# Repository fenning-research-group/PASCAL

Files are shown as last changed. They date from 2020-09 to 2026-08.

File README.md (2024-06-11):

# Perovskite Automated Spin Coat Assembly Line (PASCAL)

## Motivation

PASCAL is an automated platform for spin coating and annealing thin films onto small (>2x2 cm) substrates, aimed af increasing experimental throughput in the pursuit of designing better perovskite solar cells. Perovskite solar cells are infinitely tunable, as they can be formed with combinations of nearly half of the periodic table, presenting the excitement of limitless possibilities and the curse of dimensionality. With PASCAL, we aim to increase our experimental search rate by orders of magnitude, enabling a more systematic and exhaustive approach toward exploring the vast compositional space of interest for solar cell design.

## Hardware

### CAD schematics of PASCAL

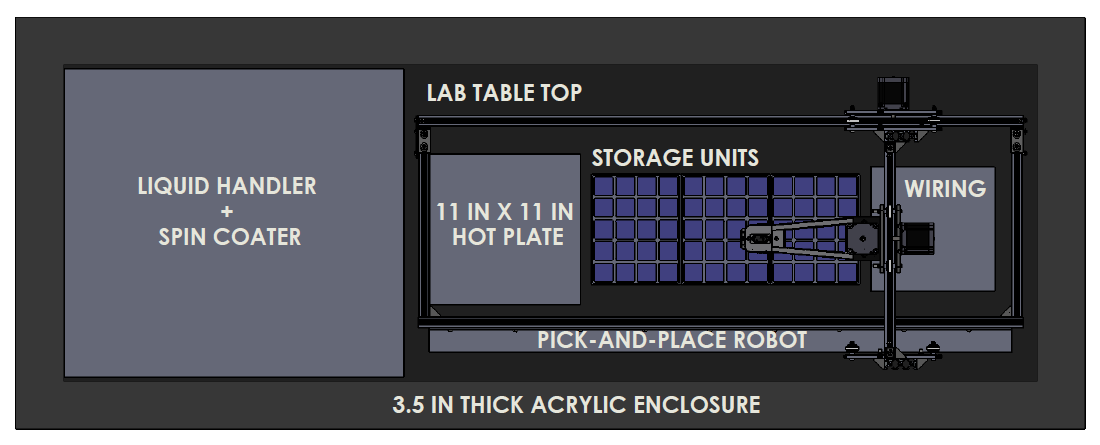
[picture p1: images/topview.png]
top view

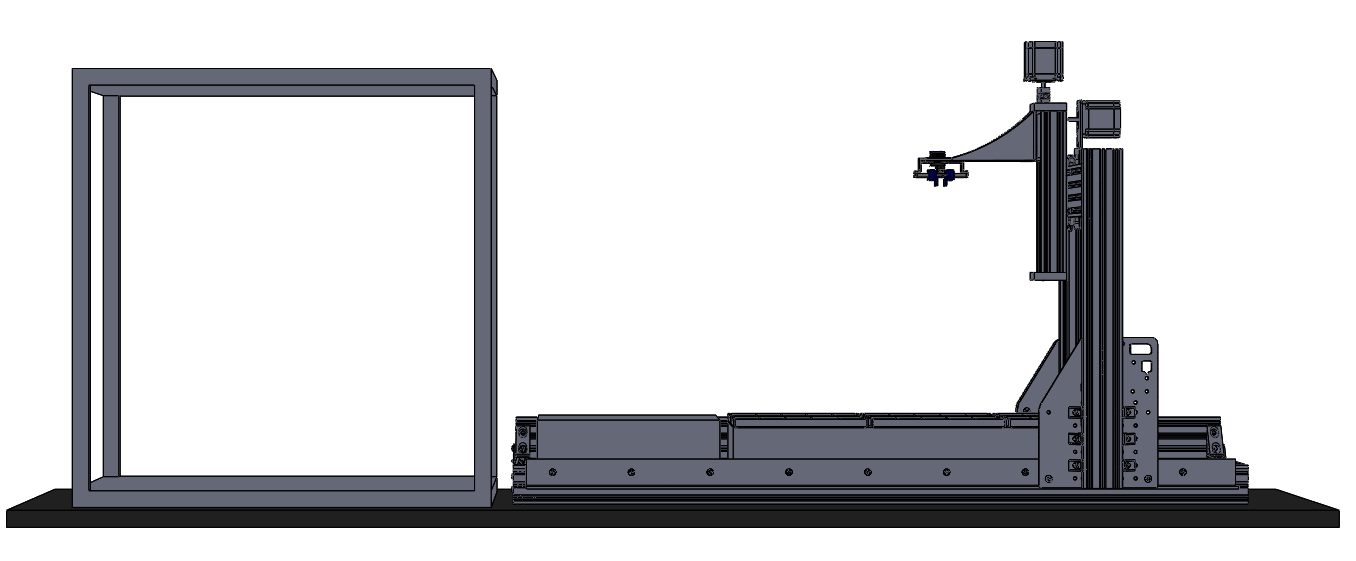
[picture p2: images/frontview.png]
front view


### Liquid handler preparing precursor solution mixtures for a compositional search

liquid handler preparing solutions for a composition spread

### Liquid handler + spincoater working in conjunction to deposit solution onto substrate.

spin coating one sample

### Automated Full Sample Fabrication + Characterization Timelapse

https://github.com/fenning-research-group/PASCAL/assets/49666626/01028334-c0f0-4b86-ad78-245d9399b324

## Experimental Planning

- Computed material properties -> manifold embedding / dimensionality reduction into "behavior space"

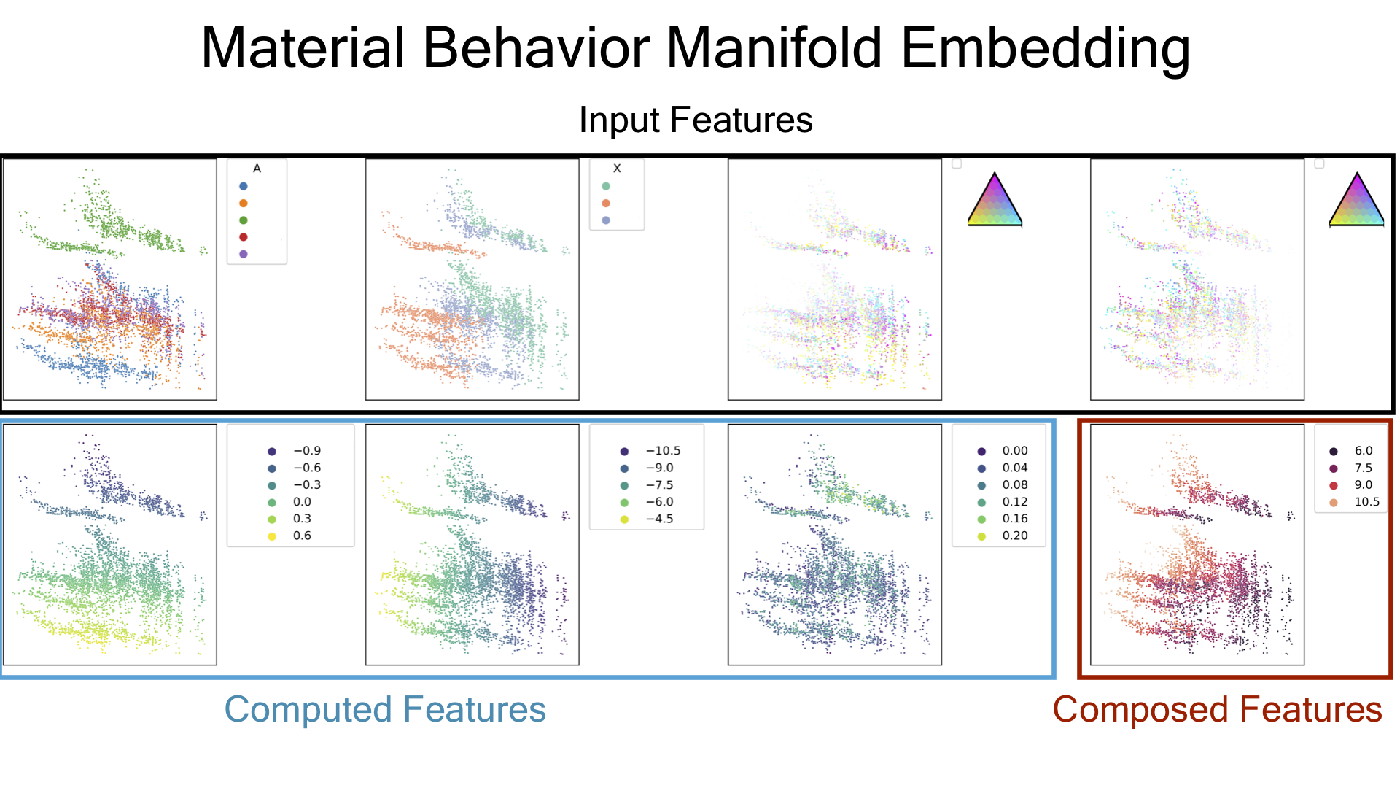
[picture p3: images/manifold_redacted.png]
manifold embedding


### Hardware Scheduling

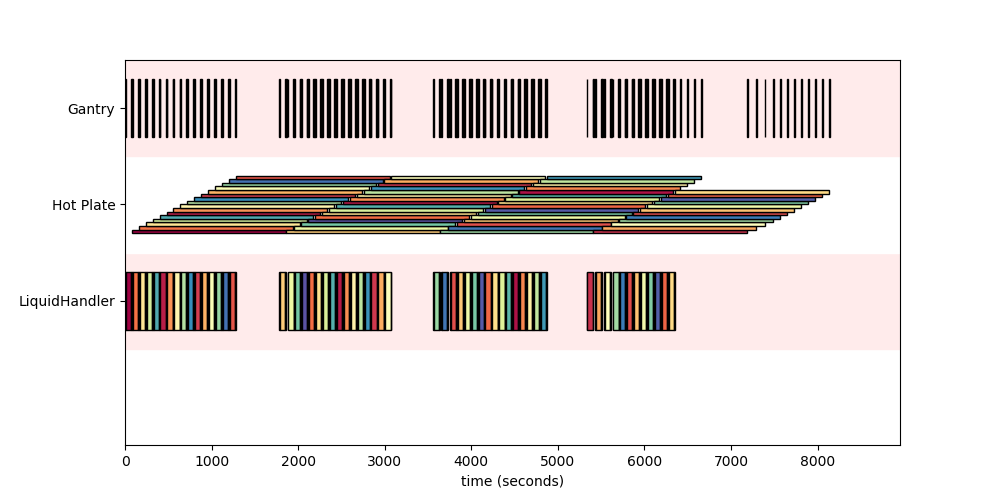
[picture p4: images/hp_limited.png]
sample fabrication scheduling to parallelize sample processes while hitting target timings


## Active Learning

### intra-run (narrow scope)

- bayesian approach to evaluating sample space
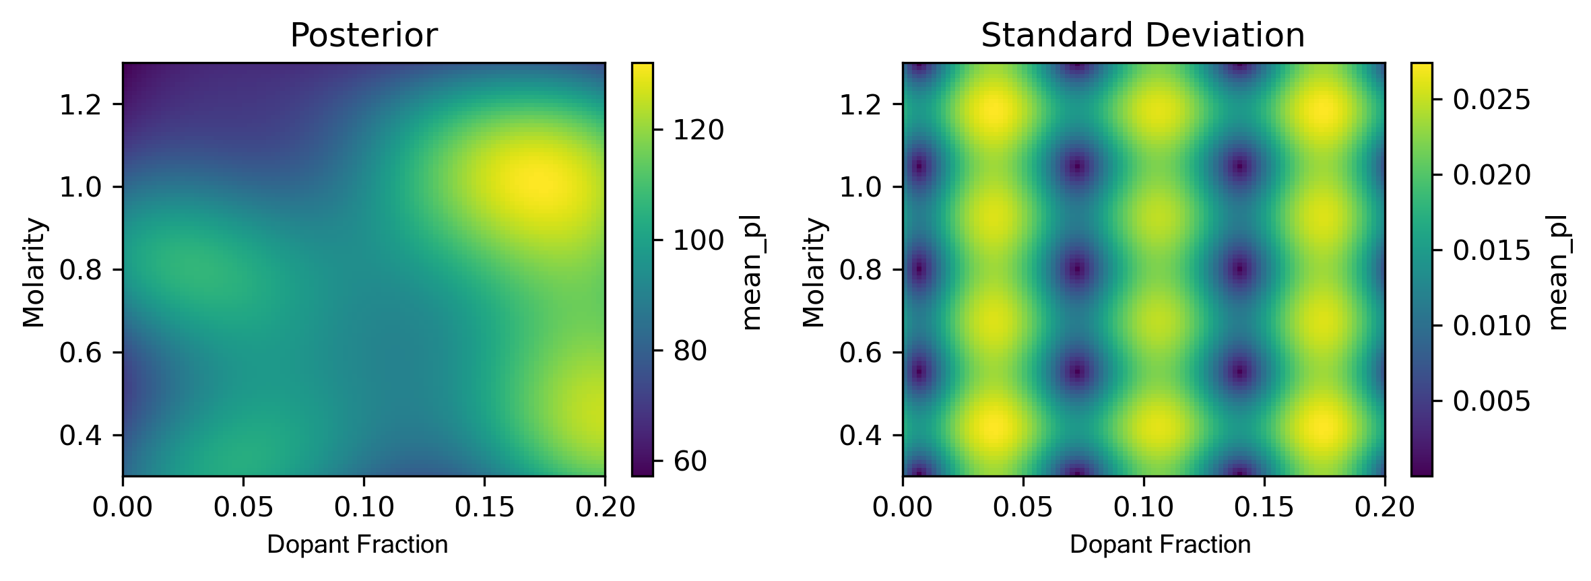
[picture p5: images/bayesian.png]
bayesian posterior fit to experimental outcome


- update compositions of interest using in-line during experiment

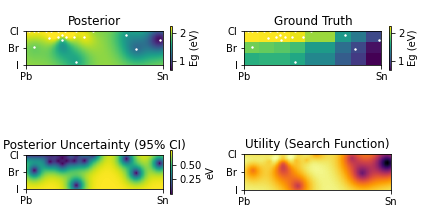
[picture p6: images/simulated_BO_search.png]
simulated bayesian optimization series


### inter-run (wide scope)

- bayesian approach with operator input (XRD, UV-Vis, etc)
- find covariances between composition/fabrication conditions
- point towards broader design philosophies in perovskite solar cells

## In-Line Characterization

- Widefield PL camera
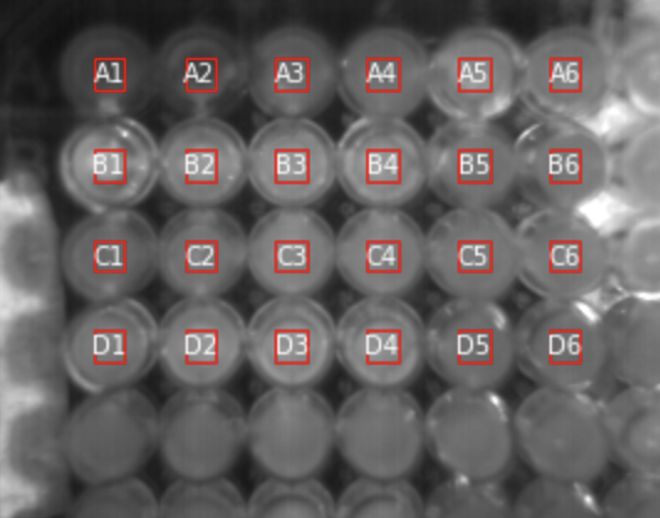
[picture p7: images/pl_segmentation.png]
segmenting PL from wells


- RGB Imaging for color determination
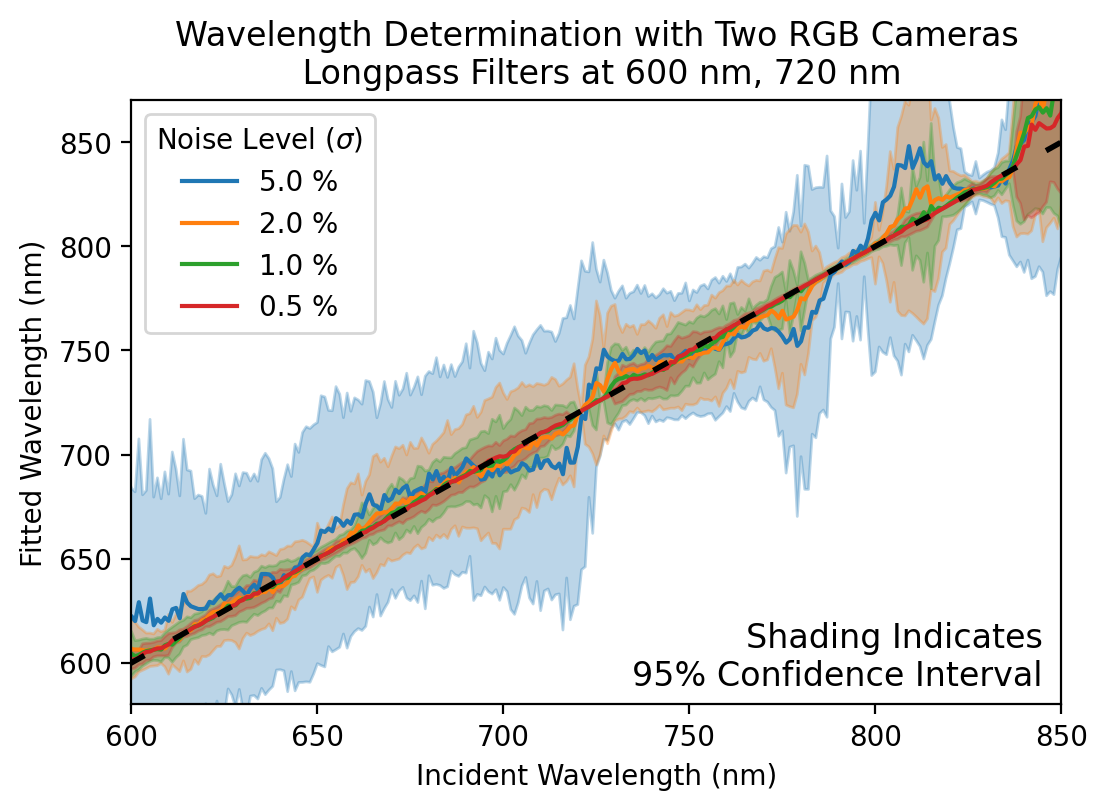
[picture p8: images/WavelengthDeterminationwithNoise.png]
PL wavelength determination with RGB cameras


## Dependency
  - python=3.7.9=h26836e1_0

## Addons 

See our [fenningresearchgroup.com/https://github.com/fenning-research-group/PASCAL_TrainView
](https://github.com/fenning-research-group/PASCAL_TrainView)https://github.com/fenning-research-group/PASCAL_TrainView

and https://github.com/dnzckn/BO-PV repo's for additional capabilities

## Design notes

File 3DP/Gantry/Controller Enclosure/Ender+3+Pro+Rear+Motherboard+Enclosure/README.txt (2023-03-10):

Ender 3 Pro Rear Motherboard Enclosure by Adarkstudio on Thingiverse: https://www.thingiverse.com/thing:4115617

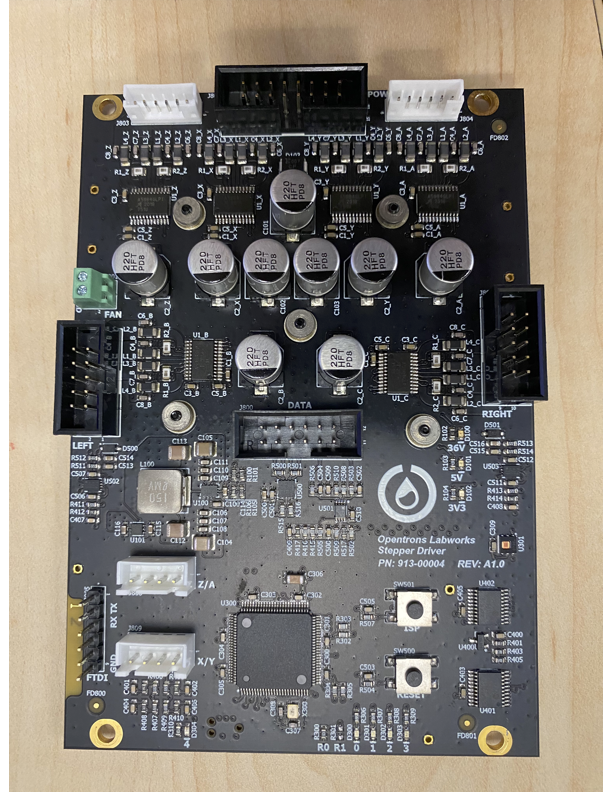
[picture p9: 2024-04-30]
hardware/liquidhandler/photos/StepperDriver.png

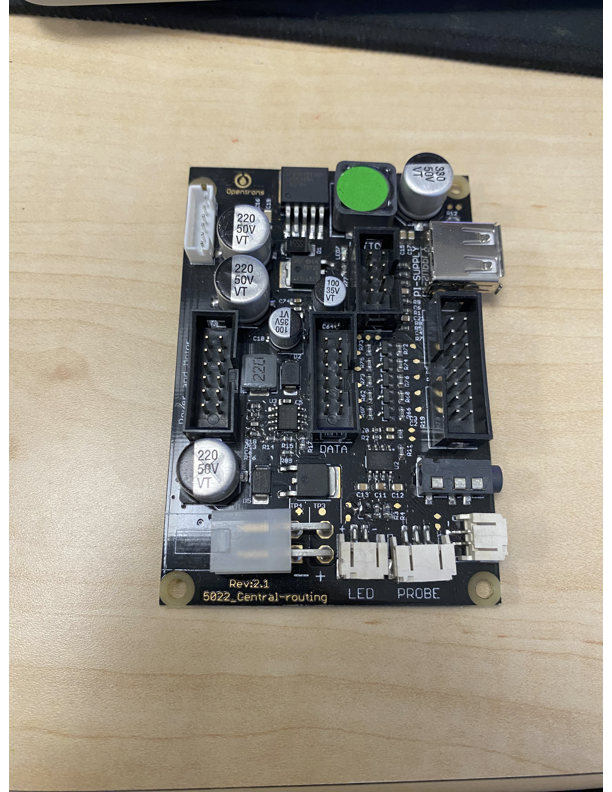
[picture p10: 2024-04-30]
hardware/liquidhandler/photos/OT_Control_Board.png

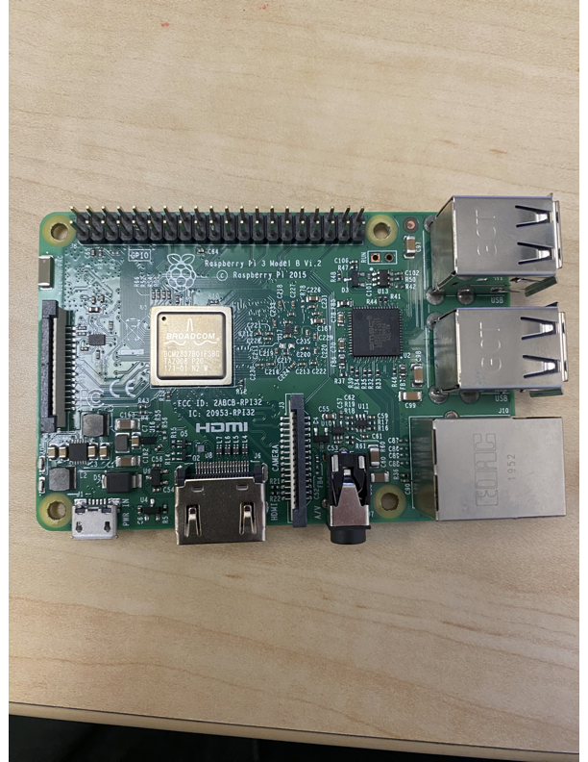
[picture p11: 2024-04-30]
hardware/liquidhandler/photos/RaspberryPi.png

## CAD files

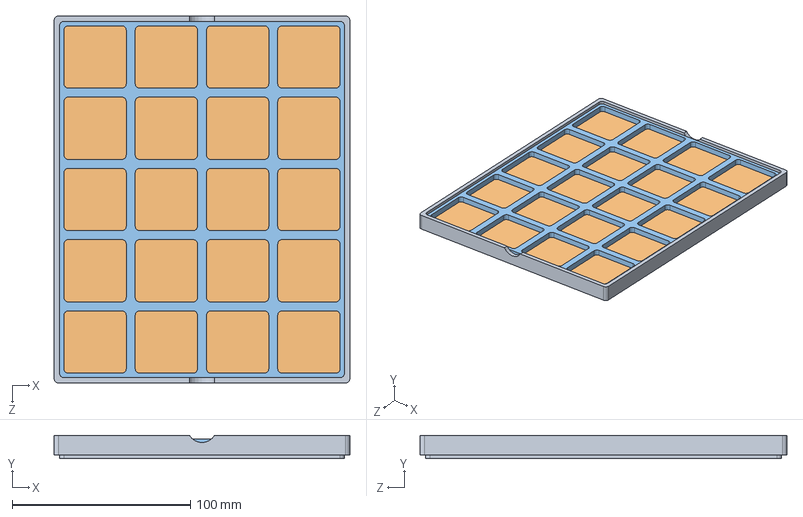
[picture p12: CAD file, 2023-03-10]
3DP/Enclosure/Complete Config (1)/storage_container/Storage Tray v2.SLDASM
166.0 x 13.0 x 206.0 mm
Storage_shell
Storage_material
Storage_spacers

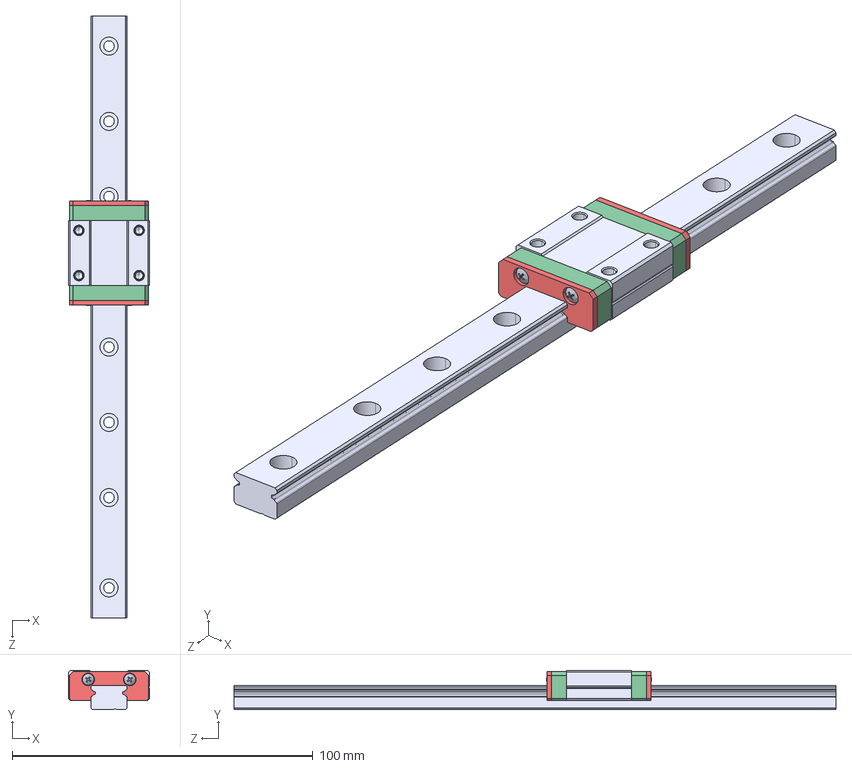
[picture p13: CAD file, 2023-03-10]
3DP/Gantry/TRANSLATION PROTO 1 FINAL/mgn12_Linear Guide/MGN12 LINEAR GUIDE SUBASSEMBLY, 12C.STEP
27.0 x 13.0 x 200.0 mm
MGN12 LINEAR GUIDE RAIL, CONFIGURABLE_200 mm
MGN12C, LINEAR GUIDE BLOCK

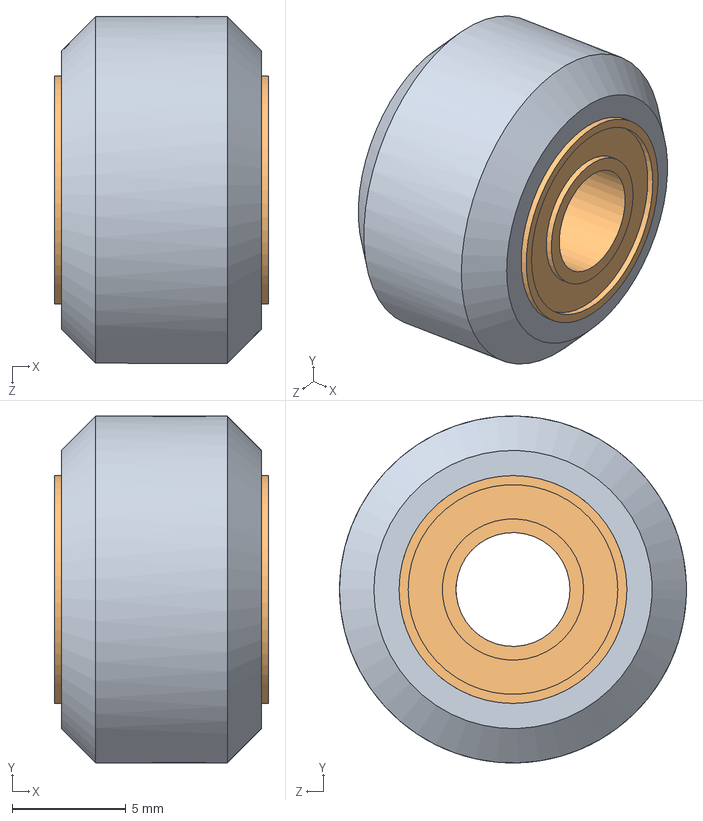
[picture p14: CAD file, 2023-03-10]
3DP/Gantry/TRANSLATION PROTO 1 FINAL/Mini V Gantry Set/Delrin Mini V Wheel Kit/Delrin Mini V Wheel Kit.SLDASM
9.40 x 15.2 x 15.2 mm
Delrin Mini V Wheel
Mini Ball Bearing 105zz 5x10x4 x 2
Mini V Wheel Precision Shim

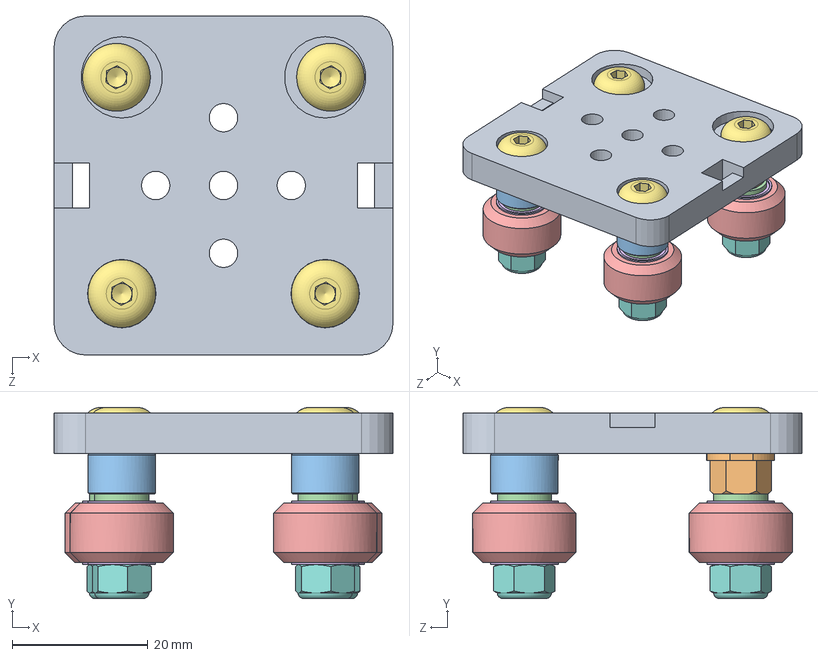
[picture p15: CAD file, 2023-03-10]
3DP/Gantry/TRANSLATION PROTO 1 FINAL/Mini V Gantry Set/Mini V Gantry Set.SLDASM
50.0 x 28.2 x 50.0 mm
Mini V Gantry Plate
Mini Eccentric Spacer 6mm x 2
Aluminum Spacer 6mm x 2
Mini V Wheel Precision Shim x 8
Delrin Mini V Wheel x 4
Mini Ball Bearing 105zz 5x10x4 x 8
M5x25 ISO7380 x 4
Nylon Insert Lock Nut M5 x 4

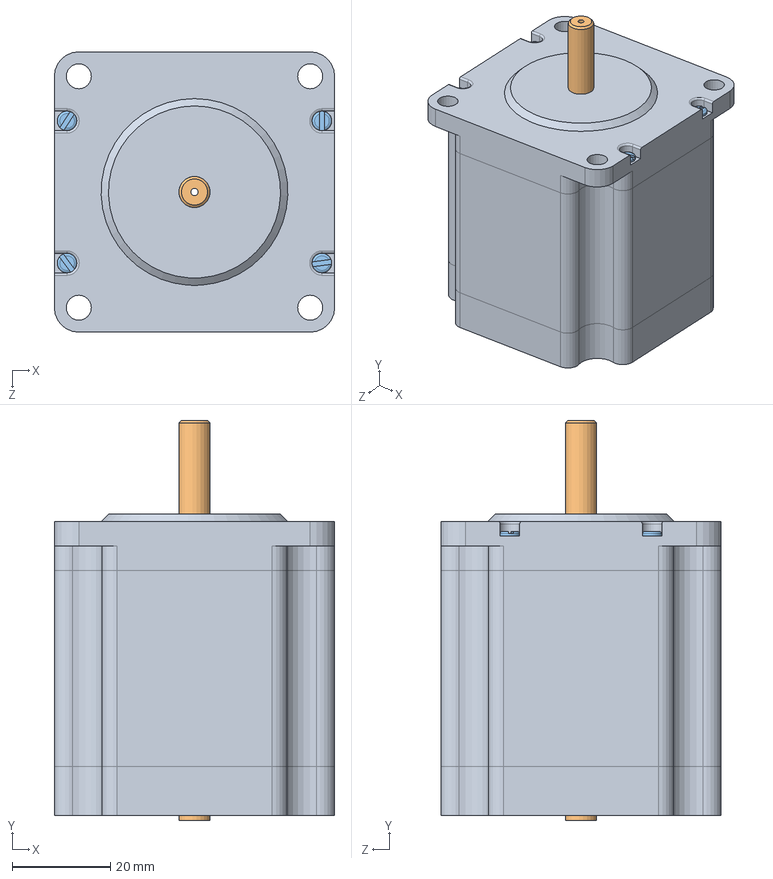
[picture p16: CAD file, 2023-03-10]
3DP/Gantry/TRANSLATION PROTO 1 FINAL/NEMA 23/NEMA23.SLDASM
57.2 x 81.6 x 57.2 mm
NEMA23
inside
Pin x 4

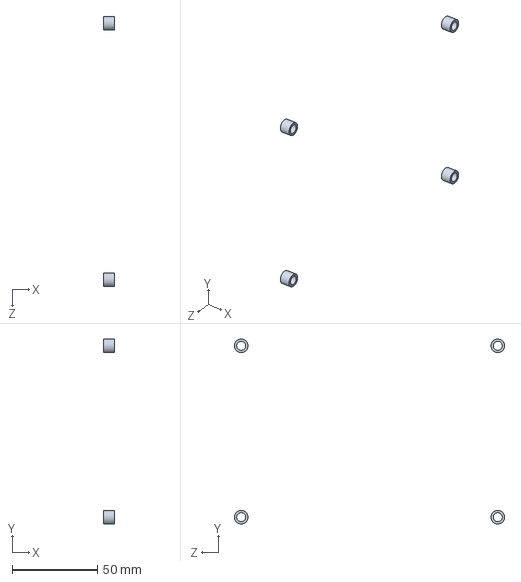
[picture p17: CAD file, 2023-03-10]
3DP/Gantry/TRANSLATION PROTO 1 FINAL/OX PLATE V2/OX Plate X Translation Inner.SLDASM
6.35 x 108.6 x 158.6 mm
6.35mm_Spacer x 4

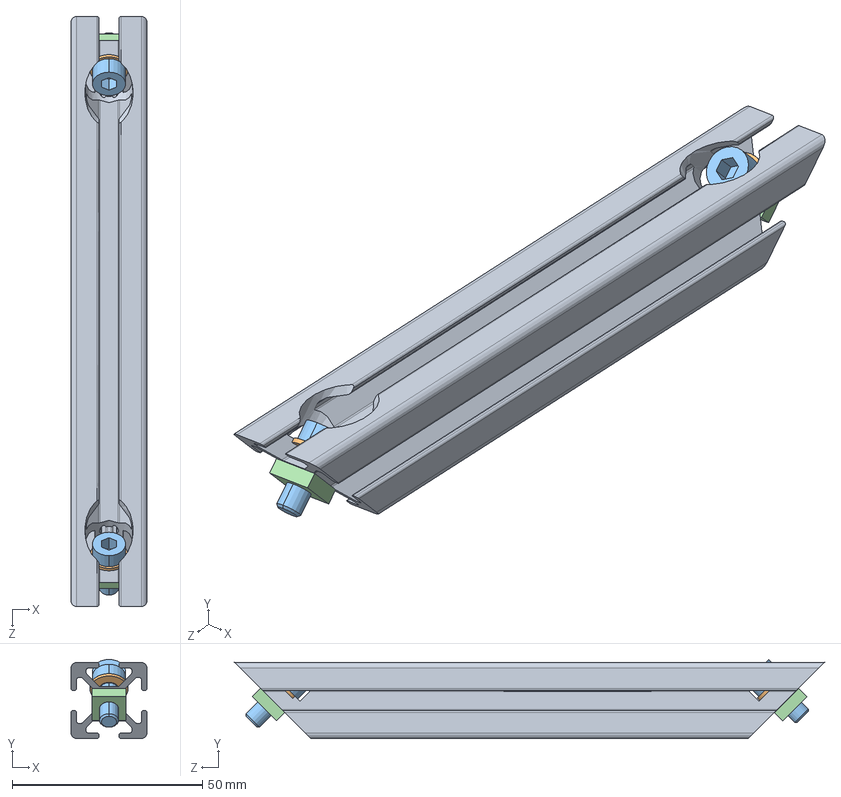
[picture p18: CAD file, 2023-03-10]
3DP/Gantry/TRANSLATION PROTO 1 FINAL/Support Bracket/20_2565_d.sldasm
20.0 x 20.8 x 155.0 mm
_20_2565_s_2

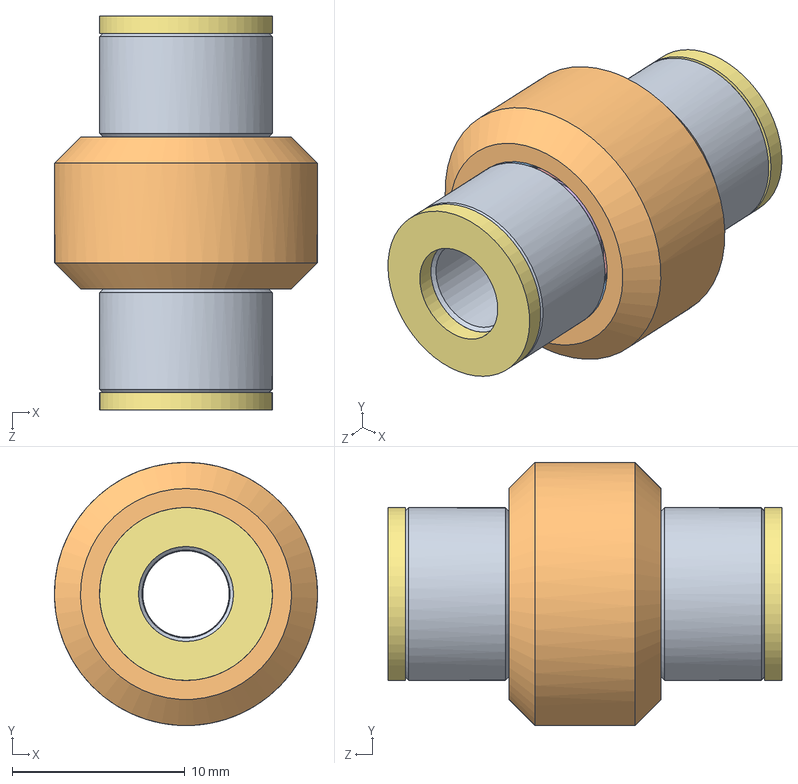
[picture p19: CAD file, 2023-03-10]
3DP/Gantry/TRANSLATION PROTO 1 FINAL/Wheel and Bearing.SLDASM
15.2 x 15.2 x 22.8 mm
Aluminum Spacer 6mm x 2
Xtreme Mini V Wheel
L_1050_3 x 2
L_1050_5 x 16
L_1050_14 x 2
L_1050_16 x 2
V Wheel Shim x 3

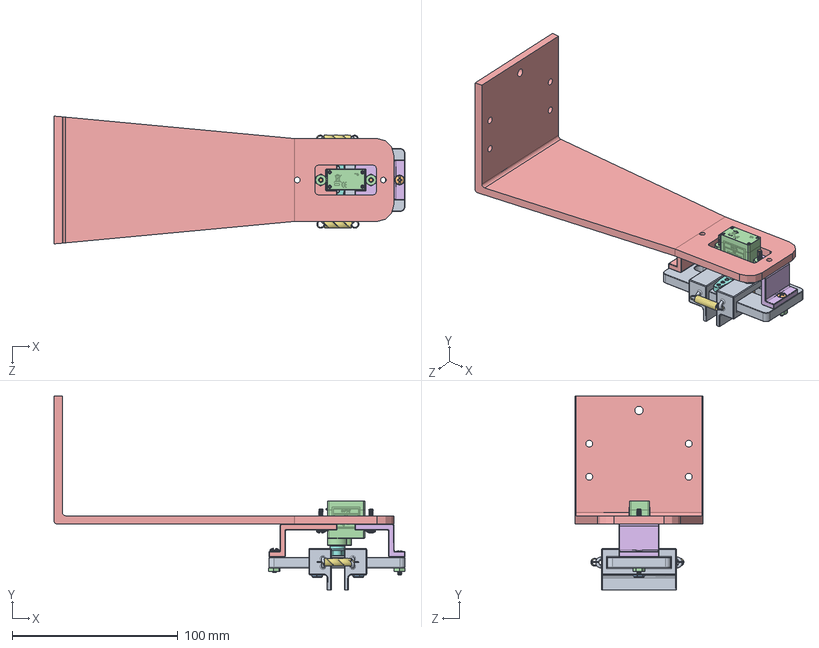
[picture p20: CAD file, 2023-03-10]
3DP/Grippers/CAd/Gripper_assembly.SLDASM
211.7 x 116.8 x 77.2 mm
Plate
ptfe_sleeve_bearing x 2
Shoulder Screw x 2
Micro Feedback Servo
left_bracket
right_bracket
tension_spring x 2
servo_horn
gripper x 2
90604A554_PAN HEAD COMBINATION PHILLIPSSLOTTED SCREWS x 4
91831A005_TYPE 18-8 STAINLESS STL NYLON-INSERT LOCKNUT x 2
91841A005_TYPE 18-8 STAINLESS STEEL HEX NUT x 4
cantilever_arm_machined

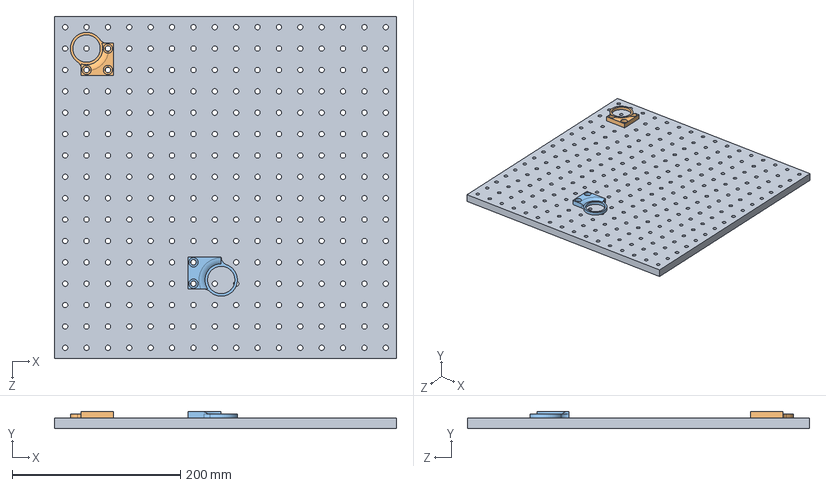
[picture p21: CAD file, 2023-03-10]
3DP/Hot Plate/Assem1.SLDASM
406.4 x 20.7 x 406.4 mm
1inchbreadboard
scilogex_foot_ring
scilogex_foot_ring_br

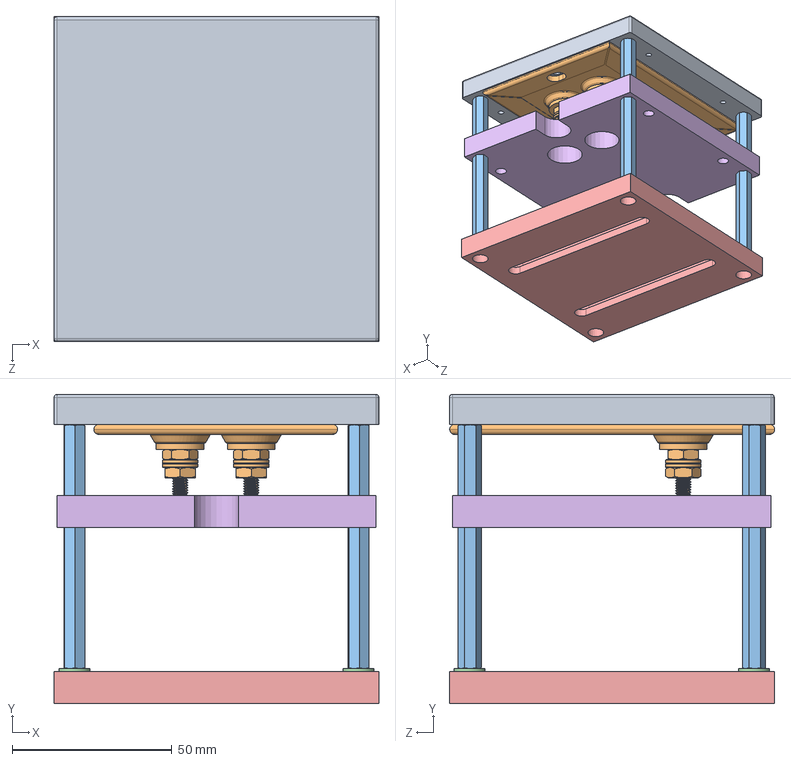
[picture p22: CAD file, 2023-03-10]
3DP/Hot Plate/DIY/HeaterAssembly.SLDASM
101.6 x 96.7 x 101.7 mm
HeatingSurface
3619K811_Bolt- and Clamp-Mount Strip Heater
93505A013_Male-Female Threaded Hex Standoff x 4
93785A300_High-Temperature PEEK Plastic Washer x 4
fiberglass_mat

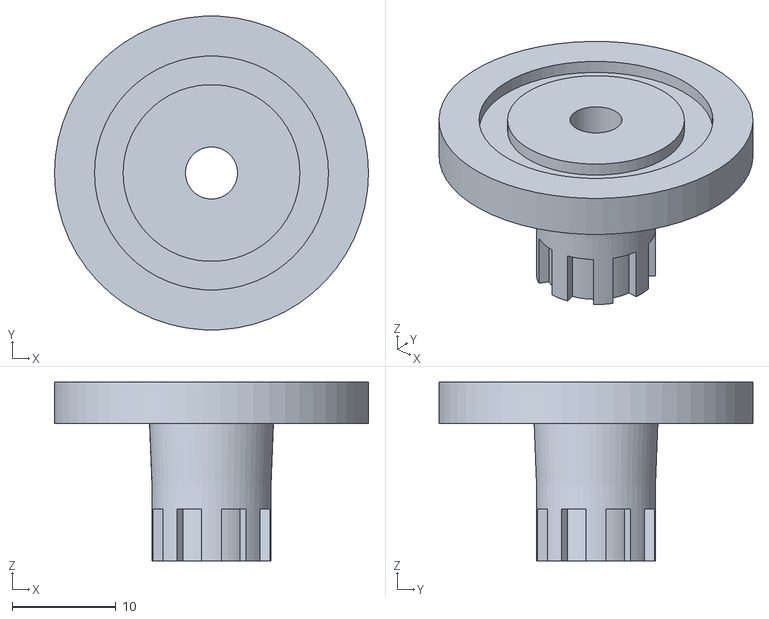
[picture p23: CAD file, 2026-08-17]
3DP/Spin Coater/fully_printed_chuck_1x1in.stl
30.2 x 30.2 x 17.2

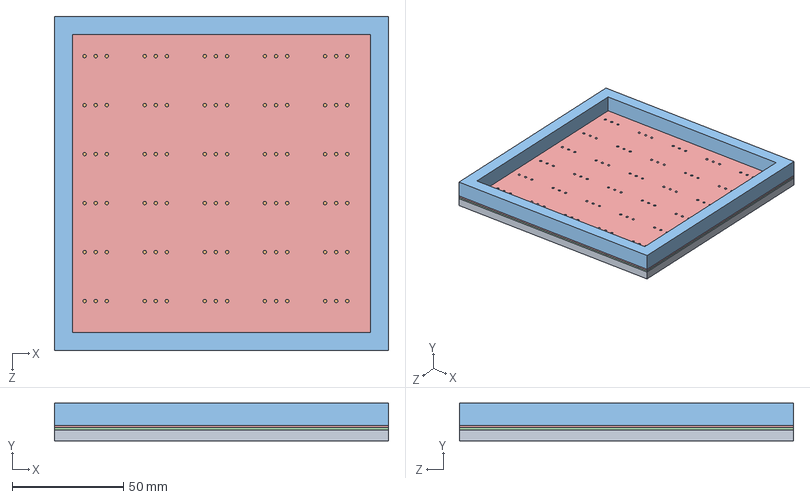
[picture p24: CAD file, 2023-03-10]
3DP/Storage/Tray v2 Rishi 2/Assem1.SLDASM
150.0 x 17.0 x 150.0 mm
Tray
175by175slide x 30
AlignmentPlate

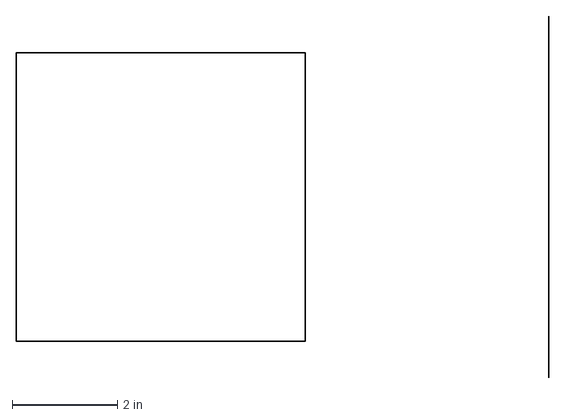
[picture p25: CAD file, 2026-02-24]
build_instructions/hotplates/cadfiles/degtop_notfull.dxf
10.1 x 6.89 in

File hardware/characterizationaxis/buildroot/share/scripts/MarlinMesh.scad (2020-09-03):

 /**************************************\
 *                                      *
 *   OpenSCAD Mesh Display              *
 *   by Thinkyhead - April 2017         *
 *                                      *
 *   Copy the grid output from Marlin,  *
 *   paste below as shown, and use      *
 *   OpenSCAD to see a visualization    *
 *   of your mesh.                      *
 *                                      *
 \**************************************/

$t = 0.15; // comment out during animation!
X = 0; Y = 1;
L = 0; R = 1; F = 2; B = 3;

//
// Sample Mesh - Replace with your own
//
measured_z = [
  [ -1.20, -1.13, -1.09, -1.03, -1.19 ],
  [ -1.16, -1.25, -1.27, -1.25, -1.08 ],
  [ -1.13, -1.26, -1.39, -1.31, -1.18 ],
  [ -1.09, -1.20, -1.26, -1.21, -1.18 ],
  [ -1.13, -0.99, -1.03, -1.06, -1.32 ]
];

//
// An offset to add to all points in the mesh
//
zadjust     = 0;

//
// Mesh characteristics
//
bed_size = [ 200, 200 ];

mesh_inset  = [ 10, 10, 10, 10 ]; // L, F, R, B

mesh_bounds = [
  [ mesh_inset[L], mesh_inset[F] ],
  [ bed_size[X] - mesh_inset[R], bed_size[Y] - mesh_inset[B] ]
];

mesh_size = mesh_bounds[1] - mesh_bounds[0];

                      // NOTE: Marlin meshes already subtract the probe offset
NAN         = 0;      // Z to use for un-measured points

//
// Geometry
//

max_z_scale   = 100;   // Scale at Time 0.5
min_z_scale   = 10;    // Scale at Time 0.0 and 1.0
thickness     = 0.5;   // thickness of the mesh triangles
tesselation   = 1;     // levels of tesselation from 0-2
alternation   = 2;     // direction change modulus (try it)

//
// Appearance
//

show_plane    = true;
show_labels   = true;
show_coords   = true;
arrow_length  = 5;

label_font_lg = "Arial";
label_font_sm = "Arial";
mesh_color    = [1,1,1,0.5];
plane_color   = [0.4,0.6,0.9,0.6];

//================================================ Derive useful values

big_z = max_2D(measured_z,0);
lil_z = min_2D(measured_z,0);

mean_value = (big_z + lil_z) / 2.0;

mesh_points_y = len(measured_z);
mesh_points_x = len(measured_z[0]);

xspace = mesh_size[X] / (mesh_points_x - 1);
yspace = mesh_size[Y] / (mesh_points_y - 1);

// At $t=0 and $t=1 scale will be 100%
z_scale_factor = min_z_scale + (($t > 0.5) ? 1.0 - $t : $t) * (max_z_scale - min_z_scale) * 2;

//
// Min and max recursive functions for 1D and 2D arrays
// Return the smallest or largest value in the array
//
function some_1D(b,i) = (i<len(b)-1) ? (b[i] && some_1D(b,i+1)) : b[i] != 0;
function some_2D(a,j) = (j<len(a)-1) ? some_2D(a,j+1) : some_1D(a[j], 0);
function min_1D(b,i) = (i<len(b)-1) ? min(b[i], min_1D(b,i+1)) : b[i];
function min_2D(a,j) = (j<len(a)-1) ? min_2D(a,j+1) : min_1D(a[j], 0);
function max_1D(b,i) = (i<len(b)-1) ? max(b[i], max_1D(b,i+1)) : b[i];
function max_2D(a,j) = (j<len(a)-1) ? max_2D(a,j+1) : max_1D(a[j], 0);

//
// Get the corner probe points of a grid square.
//
// Input  : x,y grid indexes
// Output : An array of the 4 corner points
//
function grid_square(x,y) = [
  [x * xspace, y * yspace, z_scale_factor * (measured_z[y][x] - mean_value)],
  [x * xspace, (y+1) * yspace, z_scale_factor * (measured_z[y+1][x] - mean_value)],
  [(x+1) * xspace, (y+1) * yspace, z_scale_factor * (measured_z[y+1][x+1] - mean_value)],
  [(x+1) * xspace, y * yspace, z_scale_factor * (measured_z[y][x+1] - mean_value)]
];

// The corner point of a grid square with Z centered on the mean
function pos(x,y,z) = [x * xspace, y * yspace, z_scale_factor * (z - mean_value)];

//
// Draw the point markers and labels
//
module point_markers(show_home=true) {
  // Mark the home position 0,0
  if (show_home)
    translate([1,1]) color([0,0,0,0.25])
      cylinder(r=1, h=z_scale_factor, center=true);

  for (x=[0:mesh_points_x-1], y=[0:mesh_points_y-1]) {
    z = measured_z[y][x] - zadjust;
    down = z < mean_value;
    xyz = pos(x, y, z);
    translate([ xyz[0], xyz[1] ]) {

      // Show the XY as well as the Z!
      if (show_coords) {
        color("black")
        translate([0,0,0.5]) {
          $fn=8;
          rotate([0,0]) {
            posx = floor(mesh_bounds[0][X] + x * xspace);
            posy = floor(mesh_bounds[0][Y] + y * yspace);
            text(str(posx, ",", posy), 2, label_font_sm, halign="center", valign="center");
          }
        }
      }

      translate([ 0, 0, xyz[2] ]) {
        // Label each point with the Z
        v = z - mean_value;
        if (show_labels) {

          color(abs(v) < 0.1 ? [0,0.5,0] : [0.25,0,0])
          translate([0,0,down?-10:10]) {

            $fn=8;
            rotate([90,0])
              text(str(z), 6, label_font_lg, halign="center", valign="center");

            if (v)
              translate([0,0,down?-6:6]) rotate([90,0])
                text(str(down || !v ? "" : "+", v), 3, label_font_sm, halign="center", valign="center");
          }
        }

        // Show an arrow pointing up or down
        if (v) {
          rotate([0, down ? 180 : 0]) translate([0,0,-1])
            cylinder(
              r1=0.5,
              r2=0.1,
              h=arrow_length, $fn=12, center=1
            );
        }
        else
          color([1,0,1,0.4]) sphere(r=1.0, $fn=20, center=1);
      }
    }
  }
}

//
// Split a square on the diagonal into
// two triangles and render them.
//
//     s : a square
//   alt : a flag to split on the other diagonal
//
module tesselated_square(s, alt=false) {
  add = [0,0,thickness];
  p1 = [
    s[0], s[1], s[2], s[3],
    s[0]+add, s[1]+add, s[2]+add, s[3]+add
  ];
  f1 = alt
      ? [ [0,1,3], [4,5,1,0], [4,7,5], [5,7,3,1], [7,4,0,3] ]
      : [ [0,1,2], [4,5,1,0], [4,6,5], [5,6,2,1], [6,4,0,2] ];
  f2 = alt
      ? [ [1,2,3], [5,6,2,1], [5,6,7], [6,7,3,2], [7,5,1,3] ]
      : [ [0,2,3], [4,6,2,0], [4,7,6], [6,7,3,2], [7,4,0,3] ];

  // Use the other diagonal
  polyhedron(points=p1, faces=f1);
  polyhedron(points=p1, faces=f2);
}

/**
 * The simplest mesh display
 */
module simple_mesh(show_plane=show_plane) {
  if (show_plane) color(plane_color) cube([mesh_size[X], mesh_size[Y], thickness]);
  color(mesh_color)
    for (x=[0:mesh_points_x-2], y=[0:mesh_points_y-2])
      tesselated_square(grid_square(x, y));
}

/**
 * Subdivide the mesh into smaller squares.
 */
module bilinear_mesh(show_plane=show_plane,tesselation=tesselation) {
  if (show_plane) color(plane_color) translate([-5,-5]) cube([mesh_size[X]+10, mesh_size[Y]+10, thickness]);

  if (some_2D(measured_z, 0)) {

    tesselation = tesselation % 4;
    color(mesh_color)
    for (x=[0:mesh_points_x-2], y=[0:mesh_points_y-2]) {
      square = grid_square(x, y);
      if (tesselation < 1) {
        tesselated_square(square,(x%alternation)-(y%alternation));
      }
      else {
        subdiv_4 = subdivided_square(square);
        if (tesselation < 2) {
          for (i=[0:3]) tesselated_square(subdiv_4[i],i%alternation);
        }
        else {
          for (i=[0:3]) {
            subdiv_16 = subdivided_square(subdiv_4[i]);
            if (tesselation < 3) {
              for (j=[0:3]) tesselated_square(subdiv_16[j],j%alternation);
            }
            else {
              for (j=[0:3]) {
                subdiv_64 = subdivided_square(subdiv_16[j]);
                if (tesselation < 4) {
                  for (k=[0:3]) tesselated_square(subdiv_64[k]);
                }
              }
            }
          }
        }
      }
    }

  }
}

//
// Subdivision helpers
//
function ctrz(a) = (a[0][2]+a[1][2]+a[3][2]+a[2][2])/4;
function avgx(a,i) = (a[i][0]+a[(i+1)%4][0])/2;
function avgy(a,i) = (a[i][1]+a[(i+1)%4][1])/2;
function avgz(a,i) = (a[i][2]+a[(i+1)%4][2])/2;

//
// Convert one square into 4, applying bilinear averaging
//
// Input  : 1 square (4 points)
// Output : An array of 4 squares
//
function subdivided_square(a) = [
  [ // SW square
    a[0],                          // SW
    [a[0][0],avgy(a,0),avgz(a,0)], // CW
    [avgx(a,1),avgy(a,0),ctrz(a)], // CC
    [avgx(a,1),a[0][1],avgz(a,3)]  // SC
  ],
  [ // NW square
    [a[0][0],avgy(a,0),avgz(a,0)], // CW
    a[1],                          // NW
    [avgx(a,1),a[1][1],avgz(a,1)], // NC
    [avgx(a,1),avgy(a,0),ctrz(a)]  // CC
  ],
  [ // NE square
    [avgx(a,1),avgy(a,0),ctrz(a)], // CC
    [avgx(a,1),a[1][1],avgz(a,1)], // NC
    a[2],                          // NE
    [a[2][0],avgy(a,0),avgz(a,2)]  // CE
  ],
  [ // SE square
    [avgx(a,1),a[0][1],avgz(a,3)], // SC
    [avgx(a,1),avgy(a,0),ctrz(a)], // CC
    [a[2][0],avgy(a,0),avgz(a,2)], // CE
    a[3]                           // SE
  ]
];


//================================================ Run the plan

translate([-mesh_size[X] / 2, -mesh_size[Y] / 2]) {
  $fn = 12;
  point_markers();
  bilinear_mesh();
}

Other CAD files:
3DP/Gantry/TRANSLATION PROTO 1 FINAL/Misc/NMB_L1050/L_1050.sldasm
3DP/Gantry/TRANSLATION PROTO 1 FINAL/OX/Solid V Wheel Shell.sldasm
3DP/Gantry/TRANSLATION PROTO 1 FINAL/Translation_V9.SLDASM
3DP/Spin Coater/fully_printed_chuck_10x10mm.stl
3DP/4pointprobe/4pp_backstop.SLDPRT
3DP/4pointprobe/4pp_backstop.STL
3DP/8020 mounts/bottomofgb3shelf.SLDDRW
3DP/8020 mounts/bottomofgb3shelf.SLDPRT
3DP/8020 mounts/cable tie mount.SLDPRT
3DP/8020 mounts/cable tie mount.STL
3DP/8020 mounts/cable tie mount_loopable_caphead.STL
3DP/8020 mounts/drawer_front.SLDPRT
3DP/8020 mounts/drawer_front.STL
3DP/8020 mounts/thorlabs post mount.SLDPRT
3DP/8020 mounts/thorlabs post mount.STL
3DP/8020 mounts/usb holder.SLDPRT
3DP/8020 mounts/usb holder.STL
3DP/Cameras/DT12 L-.SLDPRT
3DP/Cameras/DT12 L-Bracket.STL
3DP/Characterization Line/20210527 Sample Cart.SLDPRT
3DP/Characterization Line/20210527 Sample Cart.STL
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

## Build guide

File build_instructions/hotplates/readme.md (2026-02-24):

# Overview
This document details the Degredation Box/Hot Plate Setup. It utilizes

# Parts List
| Part                     | Price | Link|
|--------------------------|-------|----------------------------------------------------------------------------------------------------------------|
| DB-37 Board              | $*  | [)                       |
| 37 Pin Connecting Cable       | $*   | [)                     |
| SSR Relay  | $*   | [https://www.amazon.com/iFlight-1800KV-Brushless-Quadcopter-unibell/dp/B07XYYRWGP](https://www.amazon.com/iFlight-1800KV-Brushless-Quadcopter-unibell/dp/B07XYYRWGP) |
| PID Controller  | $*  | [https://www.mouser.com/ProductDetail/Cosel/PJMA600F-24?qs=DRkmTr78QARizXWjL2NKqg%3D%3D&countryCode=US&currencyCode=USD](https://www.mouser.com/ProductDetail/Cosel/PJMA600F-24?qs=DRkmTr78QARizXWjL2NKqg%3D%3D&countryCode=US&currencyCode=USD) |
| Power Cable             | $*   | [https://www.rocker.com.tw/en/product/lab-pumps/ptfe-coated-chemical-resistant-vacuum-pump/rocker-400c-ptfe-coated-vacuum-pump/](https://www.rocker.com.tw/en/product/lab-pumps/ptfe-coated-chemical-resistant-vacuum-pump/rocker-400c-ptfe-coated-vacuum-pump/) |
| Deg Box w/ Lid  | $*   | [https://www.hubs.com/manufacture/?technology=cnc-machining](https://www.hubs.com/manufacture/?technology=cnc-machining) |
| Quartz                 | $*   | [https://www.amazon.com/Assortment-Plusmart-Pressure-Plumbing-Connections/dp/B0BRN1H471/ref=sr_1_3?crid=2V931C3RGIA20&dib=eyJ2IjoiMSJ9.rMalqnjJK4ptQgIJLXaeol0CN2hMWmSikj0mL1o6aGlH5g0-8UIIJyiXwOtEuSjqxBKzqwW-IMcVi-_6pHMGr_V17O1k9zyMj5X0CCneCI-Jw45dT5PRA3iP8sXJPMMB65hSxLmY9sEAnRvApKuByc5BMIBpTVl4fiq46vQLhJXs_yEAJ9ZE8y7I4x47jYTukhg214csptJHL4ErhJntWRZFgNtJlqjsY_1cCjp2F6k.j1-vT5KaGQSVuHFfXLnOroh-s68B_fjaRGQ5Qn03ITc&dib_tag=se&keywords=o+rings&qid=1712552969&sprefix=o+ring%2Caps%2C179&sr=8-3](https://www.amazon.com/Assortment-Plusmart-Pressure-Plumbing-Connections/dp/B0BRN1H471/ref=sr_1_3?crid=2V931C3RGIA20&dib=eyJ2IjoiMSJ9.rMalqnjJK4ptQgIJLXaeol0CN2hMWmSikj0mL1o6aGlH5g0-8UIIJyiXwOtEuSjqxBKzqwW-IMcVi-_6pHMGr_V17O1k9zyMj5X0CCneCI-Jw45dT5PRA3iP8sXJPMMB65hSxLmY9sEAnRvApKuByc5BMIBpTVl4fiq46vQLhJXs_yEAJ9ZE8y7I4x47jYTukhg214csptJHL4ErhJntWRZFgNtJlqjsY_1cCjp2F6k.j1-vT5KaGQSVuHFfXLnOroh-s68B_fjaRGQ5Qn03ITc&dib_tag=se&keywords=o+rings&qid=1712552969&sprefix=o+ring%2Caps%2C179&sr=8-3) |
| Hot Plate *INSTERT*          | $*   | [https://www.amazon.com/OVERTURE-Filament-Consumables-Dimensional-Accuracy/dp/B07PGY2JP1/ref=sr_1_3_pp?dib=eyJ2IjoiMSJ9.SPz8Xg0t9pBHW5vzHC0hcqYxYtXwfa-Yil5LIAxK-nDf3JL1GTkKLyJrApjVsETM4KNQFX0PTiyEjpSvCEeJO5QKM6cQ-r08OafjWC4lTNDPu67BWv0pnhG3ZZ_HfrawVwvNJynrEMEsomfeJCVhNsTjr1BFBFbQpH87o5VaQDwiJH4rlViSL9sBvPO-Piux_RiqL3OfRC7emvw6rOVGAw8aUow_buCBNpMFJfJO4-Q.SG9CzlajxzBXdi_JxmHuRgmdlpNjiI1lcAEBselnEtU&dib_tag=se&keywords=-%2BPLA&qid=1712552942&sr=8-3&th=1](https://www.amazon.com/OVERTURE-Filament-Consumables-Dimensional-Accuracy/dp/B07PGY2JP1/ref=sr_1_3_pp?dib=eyJ2IjoiMSJ9.SPz8Xg0t9pBHW5vzHC0hcqYxYtXwfa-Yil5LIAxK-nDf3JL1GTkKLyJrApjVsETM4KNQFX0PTiyEjpSvCEeJO5QKM6cQ-r08OafjWC4lTNDPu67BWv0pnhG3ZZ_HfrawVwvNJynrEMEsomfeJCVhNsTjr1BFBFbQpH87o5VaQDwiJH4rlViSL9sBvPO-Piux_RiqL3OfRC7emvw6rOVGAw8aUow_buCBNpMFJfJO4-Q.SG9CzlajxzBXdi_JxmHuRgmdlpNjiI1lcAEBselnEtU&dib_tag=se&keywords=-%2BPLA&qid=1712552942&sr=8-3&th=1) |
| 110V Heating Pad         | $*   | [https://www.amazon.com/4inch-Normally-Closed-Electric-Solenoid/dp/B074Z5SDG3/ref=sr_1_3?crid=5POYNORA9EZL&dib=eyJ2IjoiMSJ9.JLsx3y_np7SG8hfKIUtJtWj8VtkfgF_CTbaxIyYoZ5OHgnqSQ8kOew68nTNhAhrPIDTpnumhJRObFIyRSCQiZCXshF3rObQj-HOZV87RKFJ6do-l0fcqZO3ZMh0pw_jtH8uBoLCpnQS4xYqQm-zO0h_RK_vBkP_qY5F-44N056ZKnEJHcm_twtE9Qvi0YZVwB6c-gy3uV4SWPL2bweUyBgrk076l_5p9qJ5PWumZ4mg.hs0sm7t366FhuDrl8LP-5qxEI9jizQlWJ90Q60t1cAI&dib_tag=se&keywords=12v+solenoid+valve&qid=1712552992&sprefix=12v+solenoid+valv%2Caps%2C130&sr=8-3](https://www.amazon.com/4inch-Normally-Closed-Electric-Solenoid/dp/B074Z5SDG3/ref=sr_1_3?crid=5POYNORA9EZL&dib=eyJ2IjoiMSJ9.JLsx3y_np7SG8hfKIUtJtWj8VtkfgF_CTbaxIyYoZ5OHgnqSQ8kOew68nTNhAhrPIDTpnumhJRObFIyRSCQiZCXshF3rObQj-HOZV87RKFJ6do-l0fcqZO3ZMh0pw_jtH8uBoLCpnQS4xYqQm-zO0h_RK_vBkP_qY5F-44N056ZKnEJHcm_twtE9Qvi0YZVwB6c-gy3uV4SWPL2bweUyBgrk076l_5p9qJ5PWumZ4mg.hs0sm7t366FhuDrl8LP-5qxEI9jizQlWJ90Q60t1cAI&dib_tag=se&keywords=12v+solenoid+valve&qid=1712552992&sprefix=12v+solenoid+valv%2Caps%2C130&sr=8-3) |
| RTD                  | $*   | [https://numato.com/product/16-channel-usb-relay-module/](https://numato.com/product/16-channel-usb-relay-module/) |
| Fiberglass Insulation                  | $*   | [https://numato.com/product/16-channel-usb-relay-module/](https://numato.com/product/16-channel-usb-relay-module/) |
| Screws                  | $*   | [https://numato.com/product/16-channel-usb-relay-module/](https://numato.com/product/16-channel-usb-relay-module/) |
| One Way Valve                  | $*   | [https://numato.com/product/16-channel-usb-relay-module/](https://numato.com/product/16-channel-usb-relay-module/) |
| Gas Flow Valve                  | $*   | [https://numato.com/product/16-channel-usb-relay-module/](https://numato.com/product/16-channel-usb-relay-module/) |
| Silver Tubes                  | $*   | [https://numato.com/product/16-channel-usb-relay-module/](https://numato.com/product/16-channel-usb-relay-module/) |
| Gas Flow attatchment (?)                  | $*   | [https://numato.com/product/16-channel-usb-relay-module/](https://numato.com/product/16-channel-usb-relay-module/) |

# Installation

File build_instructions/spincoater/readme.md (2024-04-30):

# Overview
This document details PASCAL's custom-designed spin coater, utilizing a drone motor for its hollow shaft which facilitates vacuum suction to secure the substrate. The motor is controlled via a rotary encoder, allowing precise substrate positioning essential for automated processing. The setup requires a Windows machine with Python to send commands; alternatively, a Raspberry Pi may be used to operate the ODrive, though this configuration remains untested.



# Parts List
| Part                     | Price | Link|
|--------------------------|-------|----------------------------------------------------------------------------------------------------------------|
| ODRIVE V3.6              | $260  | [https://odriverobotics.com/shop/odrive-v36](https://odriverobotics.com/shop/odrive-v36)                       |
| 8192 CPR ENCODER         | $40   | [https://odriverobotics.com/shop/cui-amt-102](https://odriverobotics.com/shop/cui-amt-102)                     |
| 1800kV Brushless motor   | $23   | [https://www.amazon.com/iFlight-1800KV-Brushless-Quadcopter-unibell/dp/B07XYYRWGP](https://www.amazon.com/iFlight-1800KV-Brushless-Quadcopter-unibell/dp/B07XYYRWGP) |
| Modular PS 600W 24V 25A  | $190  | [https://www.mouser.com/ProductDetail/Cosel/PJMA600F-24?qs=DRkmTr78QARizXWjL2NKqg%3D%3D&countryCode=US&currencyCode=USD](https://www.mouser.com/ProductDetail/Cosel/PJMA600F-24?qs=DRkmTr78QARizXWjL2NKqg%3D%3D&countryCode=US&currencyCode=USD) |
| Vaacum pump              | $300   | [https://www.rocker.com.tw/en/product/lab-pumps/ptfe-coated-chemical-resistant-vacuum-pump/rocker-400c-ptfe-coated-vacuum-pump/](https://www.rocker.com.tw/en/product/lab-pumps/ptfe-coated-chemical-resistant-vacuum-pump/rocker-400c-ptfe-coated-vacuum-pump/) |
| Al-Machined Motor Chuck  | $200   | [https://www.hubs.com/manufacture/?technology=cnc-machining](https://www.hubs.com/manufacture/?technology=cnc-machining) |
| O-rings                 | $8   | [https://www.amazon.com/Assortment-Plusmart-Pressure-Plumbing-Connections/dp/B0BRN1H471/ref=sr_1_3?crid=2V931C3RGIA20&dib=eyJ2IjoiMSJ9.rMalqnjJK4ptQgIJLXaeol0CN2hMWmSikj0mL1o6aGlH5g0-8UIIJyiXwOtEuSjqxBKzqwW-IMcVi-_6pHMGr_V17O1k9zyMj5X0CCneCI-Jw45dT5PRA3iP8sXJPMMB65hSxLmY9sEAnRvApKuByc5BMIBpTVl4fiq46vQLhJXs_yEAJ9ZE8y7I4x47jYTukhg214csptJHL4ErhJntWRZFgNtJlqjsY_1cCjp2F6k.j1-vT5KaGQSVuHFfXLnOroh-s68B_fjaRGQ5Qn03ITc&dib_tag=se&keywords=o+rings&qid=1712552969&sprefix=o+ring%2Caps%2C179&sr=8-3](https://www.amazon.com/Assortment-Plusmart-Pressure-Plumbing-Connections/dp/B0BRN1H471/ref=sr_1_3?crid=2V931C3RGIA20&dib=eyJ2IjoiMSJ9.rMalqnjJK4ptQgIJLXaeol0CN2hMWmSikj0mL1o6aGlH5g0-8UIIJyiXwOtEuSjqxBKzqwW-IMcVi-_6pHMGr_V17O1k9zyMj5X0CCneCI-Jw45dT5PRA3iP8sXJPMMB65hSxLmY9sEAnRvApKuByc5BMIBpTVl4fiq46vQLhJXs_yEAJ9ZE8y7I4x47jYTukhg214csptJHL4ErhJntWRZFgNtJlqjsY_1cCjp2F6k.j1-vT5KaGQSVuHFfXLnOroh-s68B_fjaRGQ5Qn03ITc&dib_tag=se&keywords=o+rings&qid=1712552969&sprefix=o+ring%2Caps%2C179&sr=8-3) |
| SLA Printed Peripherals           | $10   | [https://www.amazon.com/OVERTURE-Filament-Consumables-Dimensional-Accuracy/dp/B07PGY2JP1/ref=sr_1_3_pp?dib=eyJ2IjoiMSJ9.SPz8Xg0t9pBHW5vzHC0hcqYxYtXwfa-Yil5LIAxK-nDf3JL1GTkKLyJrApjVsETM4KNQFX0PTiyEjpSvCEeJO5QKM6cQ-r08OafjWC4lTNDPu67BWv0pnhG3ZZ_HfrawVwvNJynrEMEsomfeJCVhNsTjr1BFBFbQpH87o5VaQDwiJH4rlViSL9sBvPO-Piux_RiqL3OfRC7emvw6rOVGAw8aUow_buCBNpMFJfJO4-Q.SG9CzlajxzBXdi_JxmHuRgmdlpNjiI1lcAEBselnEtU&dib_tag=se&keywords=-%2BPLA&qid=1712552942&sr=8-3&th=1](https://www.amazon.com/OVERTURE-Filament-Consumables-Dimensional-Accuracy/dp/B07PGY2JP1/ref=sr_1_3_pp?dib=eyJ2IjoiMSJ9.SPz8Xg0t9pBHW5vzHC0hcqYxYtXwfa-Yil5LIAxK-nDf3JL1GTkKLyJrApjVsETM4KNQFX0PTiyEjpSvCEeJO5QKM6cQ-r08OafjWC4lTNDPu67BWv0pnhG3ZZ_HfrawVwvNJynrEMEsomfeJCVhNsTjr1BFBFbQpH87o5VaQDwiJH4rlViSL9sBvPO-Piux_RiqL3OfRC7emvw6rOVGAw8aUow_buCBNpMFJfJO4-Q.SG9CzlajxzBXdi_JxmHuRgmdlpNjiI1lcAEBselnEtU&dib_tag=se&keywords=-%2BPLA&qid=1712552942&sr=8-3&th=1) |
| Solenoid Valve          | $8   | [https://www.amazon.com/4inch-Normally-Closed-Electric-Solenoid/dp/B074Z5SDG3/ref=sr_1_3?crid=5POYNORA9EZL&dib=eyJ2IjoiMSJ9.JLsx3y_np7SG8hfKIUtJtWj8VtkfgF_CTbaxIyYoZ5OHgnqSQ8kOew68nTNhAhrPIDTpnumhJRObFIyRSCQiZCXshF3rObQj-HOZV87RKFJ6do-l0fcqZO3ZMh0pw_jtH8uBoLCpnQS4xYqQm-zO0h_RK_vBkP_qY5F-44N056ZKnEJHcm_twtE9Qvi0YZVwB6c-gy3uV4SWPL2bweUyBgrk076l_5p9qJ5PWumZ4mg.hs0sm7t366FhuDrl8LP-5qxEI9jizQlWJ90Q60t1cAI&dib_tag=se&keywords=12v+solenoid+valve&qid=1712552992&sprefix=12v+solenoid+valv%2Caps%2C130&sr=8-3](https://www.amazon.com/4inch-Normally-Closed-Electric-Solenoid/dp/B074Z5SDG3/ref=sr_1_3?crid=5POYNORA9EZL&dib=eyJ2IjoiMSJ9.JLsx3y_np7SG8hfKIUtJtWj8VtkfgF_CTbaxIyYoZ5OHgnqSQ8kOew68nTNhAhrPIDTpnumhJRObFIyRSCQiZCXshF3rObQj-HOZV87RKFJ6do-l0fcqZO3ZMh0pw_jtH8uBoLCpnQS4xYqQm-zO0h_RK_vBkP_qY5F-44N056ZKnEJHcm_twtE9Qvi0YZVwB6c-gy3uV4SWPL2bweUyBgrk076l_5p9qJ5PWumZ4mg.hs0sm7t366FhuDrl8LP-5qxEI9jizQlWJ90Q60t1cAI&dib_tag=se&keywords=12v+solenoid+valve&qid=1712552992&sprefix=12v+solenoid+valv%2Caps%2C130&sr=8-3) |
| 16 Channel USB Relay Module                   | $100   | [https://numato.com/product/16-channel-usb-relay-module/](https://numato.com/product/16-channel-usb-relay-module/) |

# Installation
Connect the hardware following https://docs.odriverobotics.com/v/0.5.5/getting-started.html
 - Motor wire configuration to ODrive does not matter, but encoder wires do
 - Ensure break resistor is connected&enabled, polarity does not matter
 - Ensure that the encoder is supported (use our 3D printed part)
 - Ensure that the motor can rotate with minimal friction when completely assemeled 

### Motor Control 
To enable Odrive to properly control the motor, the following parameters need to be set:

0. Start odrivetool in your terminal to set encoder settings

1. CPR of the encoder (this is the number of indexed "positions" the encoder has, for the encoder linked above, it is 8192)
- `odrv0.axis0.encoder.config.cpr = 8192`

2. Motor pole pairs (Pole pairs = number of permanent magnets in the motor/2, for the motor linked above, it is 7)
- `odrv0.axis0.motor.config.pole_pairs = 7`

3. Motor current limit and calibration current
- `odrv0.axis0.motor.config.current_lim = 40`
- `odrv0.axis0.motor.config.calibration_current = 10`

4. Motor Torque Constant (8.27/motorkV
- `odrv0.axis0.motor.config.torque_constant = 8.27 / 1800`

5. ODrive break resistance 
- `odrv0.config.enable_brake_resistor = True`
- `odrv0.config.brake_resistance = 2`

6. Motor PID Gains (adjust to 0 if the motor vibrates or spins after calibration, but start by raising P and V value from 0 if rpm control fails after calibration)

The table below contains settings that worked well for us, but we recommend fine tuning using odrivetool's live plot functions

| Motor                    | Position | Velocity  | Integrator
|--------------------------|-------|---------------|-------------------------------------------------------------------------------------------------|
| 1800kV | `odrv0.axis0.controller.config.pos_gain = 5` | `odrv0.axis0.controller.config.vel_gain = 0.05` | `odrv0.axis0.controller.config.vel_integrator_gain =  5 * vel_gain`
| 1700kV | `odrv0.axis0.controller.config.pos_gain = 100` | `odrv0.axis0.controller.config.vel_gain = 0.05` | `odrv0.axis0.controller.config.vel_integrator_gain =  0`

7. Save the settings
- `odrv0.save_configuration()`

8. Test Calibration
- `odrv0.axis0.requested_state = AXIS_STATE_ENCODER_OFFSET_CALIBRATION` #Should rotate CW and CCW

9. Test Control Mode
- `odrv0.axis0.requested_state = AXIS_STATE_CLOSED_LOOP_CONTROL`

* See https://docs.odriverobotics.com/v/0.5.5/getting-started.html for more details.

10. Proceed to Python Code if no issues
Go to Example Usage at bottom

### Vacuum and Solenoid Control
1. Connect a 12v 1A power supply to the solenoid valve by connecting its + terminal to the solenoid + terminal then connect the solenoid's - terminal to the relay module slot 7. 
2. Connect the relay modules's slot 7 - terminal to the power supplys - terminal.
3. Connect the relay modules's usb to the computer. 
4. Ensure that your PC has the driver for the module, if not, download it from https://numato.com/product/16-channel-usb-relay-module/ 
5. Connect vacuum tubing form the pump to the solenoid valve, then from the solenoid valve to the motor chuck.

### Peripherals 
1. Get the aluminum spin coater chuck machined, ensure that the NPT is tapped for the vacuum valve and that M5 screws are tapped to fasten the encoder to the chuck.
2. Remove the screw underneath the motor shaft to allow for vacuum to be pulled through the motor.
3. Place an gasket or o-ring on the chuck to ensure a tight seal with the motor. We've found a gasket (sheet of soft rubber like material) works better (~3cm square).
4. Screw the motor down to the chuck. Ensure that the screw underneath the motor shaft is removed. 
5. Place encoder onto the chuck. 
6. Screw on the [M5 hex shaft](https://www.mcmaster.com/catalog/130/3659/90111A331) to the remaining threads of the motor shaft.
7. Place the spincoater plate (3D printed part) onto the hex shaft (pressure fit)
8. Glue on an o-ring to the top of the hex shaft to ensure a tight seal with the substrate (plate should be flush with top of the o-ring so that substrate is level with the plate)
9. 3D print the encoder mount and screw it down to the chuck. Glue magnets into place.
10. 3D print the spin coater bowl. Glue magnets into place.
11. Using the magnets attach the bowl to the encoder mount. 

# Example Usage
`ipython #if not in it`

`cd "C:\Users\Fenning lab\Documents\GitHub\PASCAL\build_instructions\spin_coater"`

`from standalone_spincoater import SpinCoater`

`sc = SpinCoater()`

`sc.set_rpm(rpm = 2000, acceleration = 1000)`

This can be combined with our SpinCoater.stop() command which will decelerate the motor to a stop and then lock the motor to a predefined position. 

Combining these two commonds a typical spin coating sequence would look like:

`sc.set_rpm(rpm = 2000, acceleration = 1000)`

`time.sleep(10)`

`sc.stop()`

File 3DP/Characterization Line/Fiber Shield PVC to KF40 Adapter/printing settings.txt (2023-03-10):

Printing settings:
	Print each half with the open slot facing down (flat side on bottom). 
	Use tree style supports.

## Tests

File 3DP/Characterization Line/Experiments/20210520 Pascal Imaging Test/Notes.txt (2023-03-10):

sample = Moses old 5% Cl MACsPbI0.8Br0.15Cl0.05. Film. Outside glovebox, looked dark but hazy on front side.

 2x 500 nm Longpasses, 10x and 40x objectives on thorlabs camera
 - note that with two adapters (SM1->Cmount->RMS), the working distance for the lens is too long. probably more zoomed than nominal

10x has ~ 1.25 mm vertical FOV (from imaging grading on thorlabs SM1 spanner)

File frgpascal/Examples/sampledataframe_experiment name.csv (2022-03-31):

 | name | storage_tray | storage_slot | substrate | worklist | spincoat0_drop0_time | spincoat0_drop0_height | spincoat0_drop0_rate | spincoat0_drop0_volume | spincoat0_drop0_molarity | spincoat0_drop0_solutes | spincoat0_drop0_solutes_dict | spincoat0_drop0_solvent | spincoat0_drop0_solvent_dict | spincoat1_drop0_time | spincoat1_drop0_height | spincoat1_drop0_rate | spincoat1_drop0_volume | spincoat1_drop0_molarity | spincoat1_drop0_solutes | spincoat1_drop0_solutes_dict | spincoat1_drop0_solvent | spincoat1_drop0_solvent_dict | spincoat1_drop1_time | spincoat1_drop1_height | spincoat1_drop1_rate | spincoat1_drop1_volume | spincoat1_drop1_molarity | spincoat1_drop1_solutes | spincoat1_drop1_solutes_dict | spincoat1_drop1_solvent | spincoat1_drop1_solvent_dict | spincoat2_drop0_time | spincoat2_drop0_height | spincoat2_drop0_rate | spincoat2_drop0_volume | spincoat2_drop0_molarity | spincoat2_drop0_solutes | spincoat2_drop0_solutes_dict | spincoat2_drop0_solvent | spincoat2_drop0_solvent_dict
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

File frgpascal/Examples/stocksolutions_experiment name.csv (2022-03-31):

Labware | Well | Volume (uL) | Solutes | Molarity (M) | Solvent
4mL_Tray1 | C2 | 610 | {'PCBM': 30.0} | 30 | {'Chlorobenzene': 1.0}
4mL_Tray1 | B3 | 1130 | {'MEO-': 1.2, 'PAcZ': 0.6} | 0.6 | {'IPA': 1.0}
4mL_Tray1 | A1 | 770 | {'FA': 0.9359999999999999, 'Cs': 0.144, 'MA': 0.12, 'Pb': 1.308, 'I': 3.1392000000000007, 'Br': 0.5886, 'Cl': 0.19620000000000004} | 1.2 | {'DMF': 0.75, 'DMSO': 0.25}
4mL_Tray1 | D1 | 3650 | {} | 0 | {'MethylAcetate': 1.0}

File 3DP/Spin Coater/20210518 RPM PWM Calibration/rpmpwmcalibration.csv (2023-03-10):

Datetime | Target RPM | Actual RPM | PWM Signal
2021/5/18 1:11:6 | 0.00 | 0.00 | 700
2021/5/18 1:11:6 | 0.00 | 0.00 | 700
2021/5/18 1:11:6 | 0.00 | 0.00 | 700
2021/5/18 1:11:6 | 0.00 | 0.00 | 700
2021/5/18 1:11:7 | 0.00 | 0.00 | 700
2021/5/18 1:11:7 | 0.00 | 0.00 | 700
2021/5/18 1:11:7 | 0.00 | 0.00 | 700
2021/5/18 1:11:7 | 0.00 | 0.00 | 700
2021/5/18 1:11:8 | 0.00 | 0.00 | 700
2021/5/18 1:11:8 | 0.00 | 0.00 | 700
2021/5/18 1:11:8 | 0.00 | 0.00 | 700
2021/5/18 1:11:8 | 0.00 | 0.00 | 700
2021/5/18 1:11:9 | 0.00 | 0.00 | 700
2021/5/18 1:11:9 | 0.00 | 0.00 | 700
2021/5/18 1:11:9 | 0.00 | 0.00 | 700
2021/5/18 1:11:9 | 0.00 | 0.00 | 700
2021/5/18 1:11:10 | 0.00 | 0.00 | 700
2021/5/18 1:11:10 | 0.00 | 0.00 | 700
2021/5/18 1:11:10 | 0.00 | 0.00 | 700
2021/5/18 1:11:10 | 0.00 | 0.00 | 700
2021/5/18 1:11:6 | 0.00 | 0.00 | 700
2021/5/18 1:11:6 | 0.00 | 0.00 | 700
2021/5/18 1:11:6 | 0.00 | 0.00 | 700
2021/5/18 1:11:6 | 0.00 | 0.00 | 700
2021/5/18 1:11:7 | 0.00 | 0.00 | 700
2021/5/18 1:11:7 | 0.00 | 0.00 | 700
2021/5/18 1:11:7 | 0.00 | 0.00 | 700
2021/5/18 1:11:7 | 0.00 | 0.00 | 700
2021/5/18 1:11:8 | 0.00 | 0.00 | 700
2021/5/18 1:11:8 | 3000.00 | 0.00 | 1168
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

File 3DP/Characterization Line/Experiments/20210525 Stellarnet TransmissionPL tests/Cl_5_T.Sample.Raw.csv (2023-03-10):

nm | A
800.000000 | 0.040924
797.500000 | 0.040581
795.000000 | 0.040885
792.500000 | 0.041151
790.000000 | 0.043596
787.500000 | 0.045027
785.000000 | 0.047046
782.500000 | 0.048895
780.000000 | 0.050176
777.500000 | 0.053942
775.000000 | 0.057242
772.500000 | 0.060428
770.000000 | 0.065576
767.500000 | 0.069332
765.000000 | 0.075018
762.500000 | 0.083354
760.000000 | 0.089358
757.500000 | 0.098110
755.000000 | 0.108822
752.500000 | 0.120710
750.000000 | 0.133543
747.500000 | 0.149140
745.000000 | 0.167816
742.500000 | 0.188287
740.000000 | 0.212625
737.500000 | 0.239507
735.000000 | 0.268575
732.500000 | 0.300395
730.000000 | 0.334134
727.500000 | 0.368617
725.000000 | 0.402297
722.500000 | 0.433516
720.000000 | 0.461713
717.500000 | 0.484253
715.000000 | 0.502710
712.500000 | 0.517870
710.000000 | 0.529239
707.500000 | 0.536954
705.000000 | 0.543670
702.500000 | 0.547920
700.000000 | 0.551385
697.500000 | 0.555614
695.000000 | 0.558664
692.500000 | 0.562998
690.000000 | 0.565605
687.500000 | 0.569528
685.000000 | 0.572967
682.500000 | 0.576469
680.000000 | 0.579992
677.500000 | 0.583695
675.000000 | 0.587466
672.500000 | 0.592593
670.000000 | 0.595563
667.500000 | 0.600313
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

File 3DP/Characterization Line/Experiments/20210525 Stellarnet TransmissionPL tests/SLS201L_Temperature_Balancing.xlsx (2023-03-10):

 | SLS201L Output With and Without Filters
 |  | No Filter | -132 mired Filter | -160 mired Filter
 | Wavelength (nm) | Power (a.u.) | Power (a.u.) | Power (a.u.)
 | 346.14 | 0.03004 | 0.001443757847 | 0.0005421820468
 | 347.64 | 0.04153 | 0.002452429975 | 0.0009729665012
 | 349.14 | 0.04576 | 0.003263532272 | 0.001367968659
 | 350.64 | 0.04869 | 0.004147710722 | 0.001824449844
Product Raw Data | 352.14 | 0.05119 | 0.005146897014 | 0.002376120015
Temperature-Balancing Filters Example | 353.64 | 0.05436 | 0.006367161251 | 0.003067568503
 | 355.14 | 0.05639 | 0.007610943075 | 0.003820724186
Item # | 356.64 | 0.05791 | 0.008908396643 | 0.004644990634
DISCLAIMER: The data presented here are typical. Slight variations in performance data will occur from lot to lot. Please contact Technical Support with any questions regarding the use or reliability of this data. | 358.14 | 0.06048 | 0.01047937202 | 0.005652108806
 | 359.64 | 0.06429 | 0.0123955061 | 0.006912539234
 | 361.13 | 0.06769 | 0.01442158803 | 0.008275321139
 | 362.63 | 0.06669 | 0.0155381958 | 0.009160959214
 | 364.13 | 0.06966 | 0.01764604829 | 0.0106774228
 | 365.63 | 0.07318 | 0.02005133683 | 0.01242682313
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

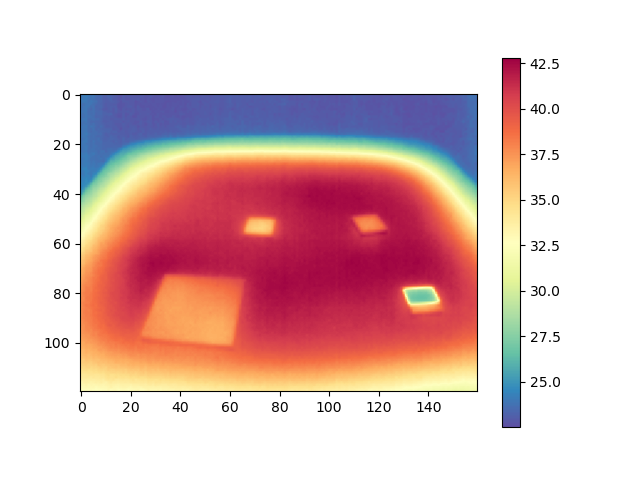
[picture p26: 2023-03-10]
3DP/Characterization Line/Infrared Camera/Example Data/Example Hotplate Tracking Image.png

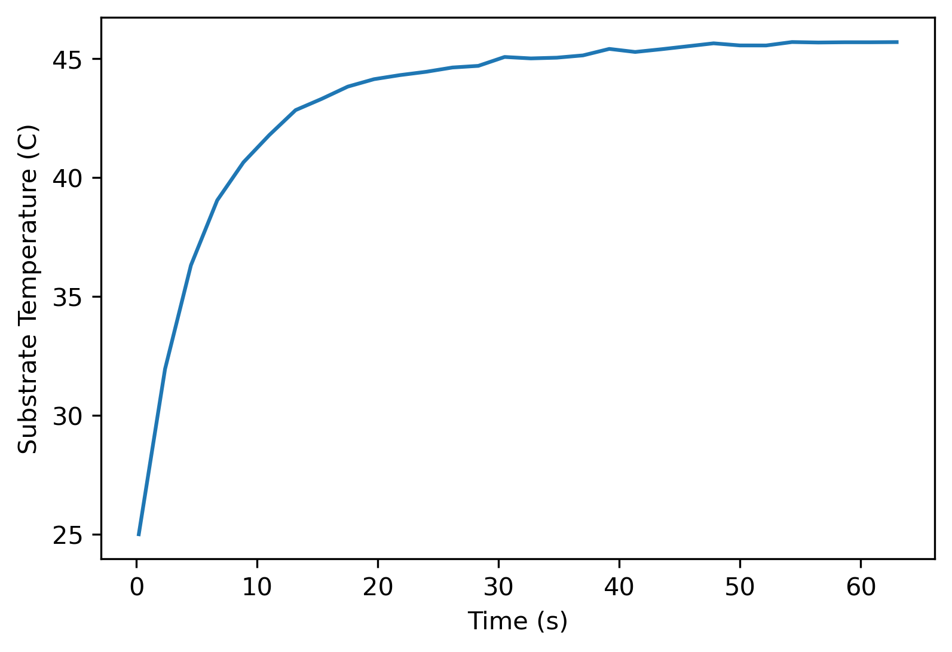
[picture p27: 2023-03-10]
3DP/Characterization Line/Infrared Camera/Example Data/Extracted Temperature Trace.png

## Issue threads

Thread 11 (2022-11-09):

### ISSUE TITLE
Brightfield inhomogeneity metric not computed on correct slice of image

### ISSUE THREAD

**Issue by kcw1375** [fenning-research-group/PASCAL#11]
Currently the inhomogeneity metric is computed only on a slice of the brightfield images to ignore parts outside the sample.
https://github.com/fenning-research-group/PASCAL/blob/45a479e4029c17791d0230e4c22e848e8014ce4a/frgpascal/analysis/brightfield.py#L9-L11

This used to make sense when our magnification was lower.
![good_slice](https://user-images.githubusercontent.com/73185476/197255774-dcd1db22-711c-46c7-9d24-d32c1e10c3b2.png)

However, now that we've increased our magnification for bf images, this slice ignores a large chunk of the sample, which means that morphological defects near the corners are neglected! 
![bad_slice](https://user-images.githubusercontent.com/73185476/197251042-68d2f20a-16b3-4131-9a27-ad31aa0bda54.png)

**Comment by kcw1375** [comment]
The above pull request is a fix which just expands the boundaries to cover the whole image.

Assuming our magnification stays consistent from now on (or at least the FOV is always  contained entirely within the sample), it should work, although it won't be backwards compatible.

**Comment by dnzckn** [comment]
can you instead pull request this to the cam swap branch, the cam swap branch assumes the higher mag optics

**Comment by kcw1375** [comment]
pull request created

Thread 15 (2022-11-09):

### ISSUE TITLE
plimg load doesnt work with different exposure times

### ISSUE THREAD

**Issue by dnzckn** [fenning-research-group/PASCAL#15]
the exposure time is saved to the PL image file name e.g. `*1000ms.tif` 

need a robust string reading to be able to load in pl images regardless of exposure, so something to look for just ms.tif for example, then to find the correct exposure.

![image](https://user-images.githubusercontent.com/49666626/200812346-ea7b4c20-feda-43c9-9774-9306881e2991.png)

**Comment by dnzckn** [comment]
in `PASCAL\frgpascal\analysis\processing.py`

**Comment by kcw1375** [comment]
pretty simple regex job. will there ever be more than one exposure per sample?

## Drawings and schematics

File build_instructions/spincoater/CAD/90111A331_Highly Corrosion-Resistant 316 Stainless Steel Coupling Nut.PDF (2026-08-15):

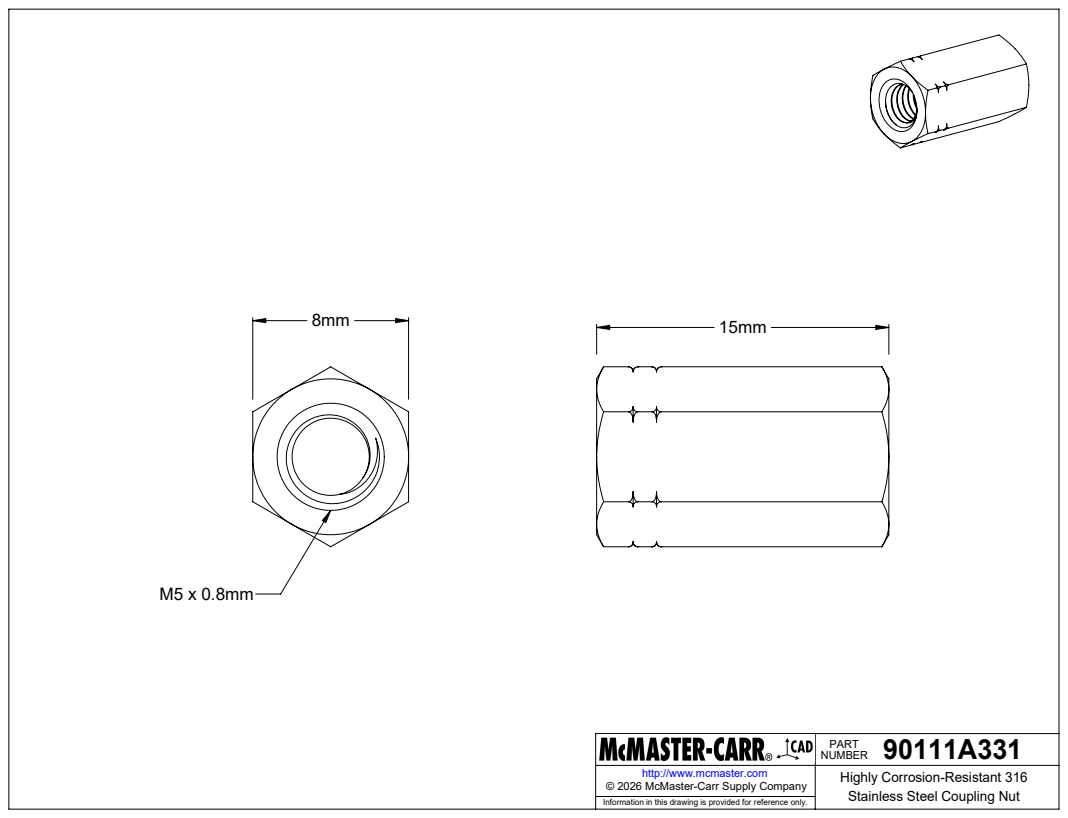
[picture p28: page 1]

90111A331 PART NUMBER

http://www.mcmaster.com | Highly Corrosion-Resistant 316 Stainless Steel Coupling Nut © 2026 McMaster-Carr Supply Company

Information in this drawing is provided for reference only.

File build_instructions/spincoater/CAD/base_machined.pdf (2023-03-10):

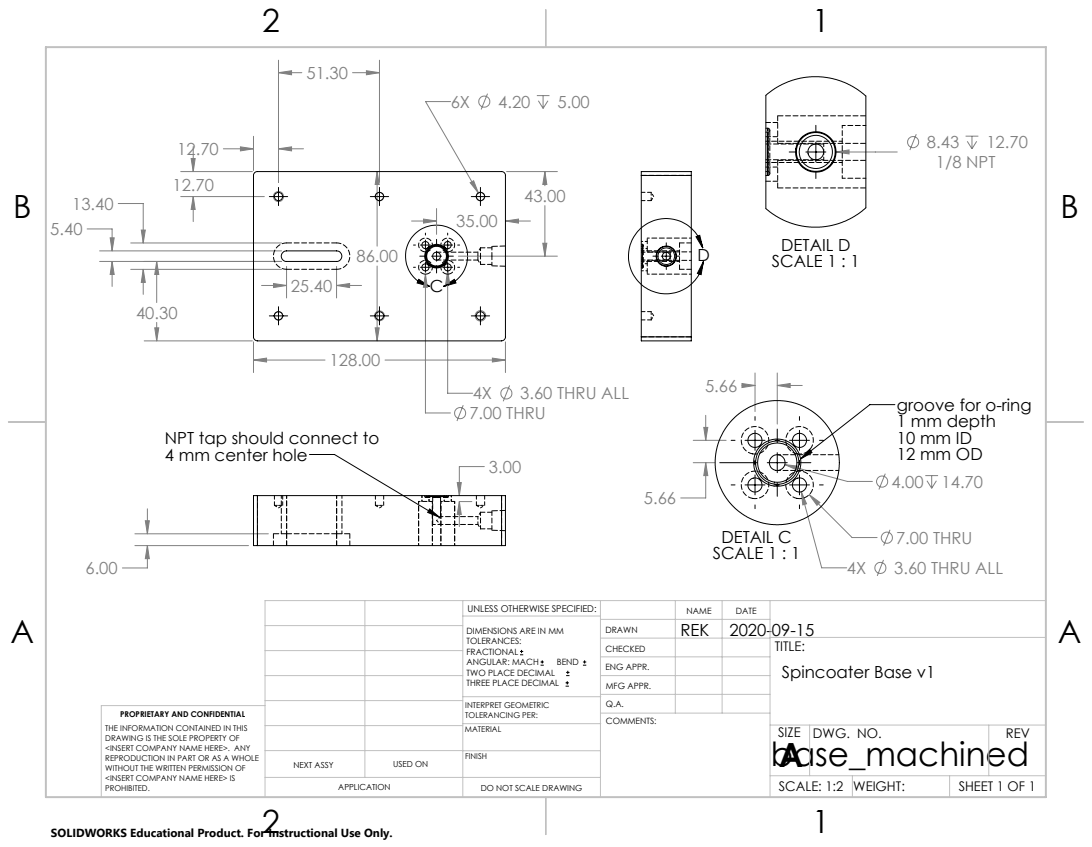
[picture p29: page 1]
3.60 THRU ALL; 7.00 THRU; DETAIL C SCALE 1 : 1; 8.43 12.70 1/8 NPT; DETAIL D SCALE 1 : 1

groove for o-ring
1 mm depth

NPT tap should connect to
4 mm center hole

UNLESS OTHERWISE SPECIFIED: | | NAME | DATE
DIMENSIONS ARE IN MM TOLERANCES: FRACTIONAL ANGULAR: MACH BEND TWO PLACE DECIMAL THREE PLACE DECIMAL | DRAWN

CHECKED | | | TITLE: Spincoater Base v1

ENG APPR.
MFG APPR.

INTERPRET GEOMETRIC TOLERANCING PER: | Q.A.
MATERIAL | | SIZE base_machined A | DWG. NO. | REV

PROPRIETARY AND CONFIDENTIAL
THE INFORMATION CONTAINED IN THIS
DRAWING IS THE SOLE PROPERTY OF
<INSERT COMPANY NAME HERE>. ANY
REPRODUCTION IN PART OR AS A WHOLE
WITHOUT THE WRITTEN PERMISSION OF
<INSERT COMPANY NAME HERE> IS
PROHIBITED.

NEXT ASSY | USED ON | FINISH

APPLICATION | DO NOT SCALE DRAWING | | SCALE: 1:2 | WEIGHT: | SHEET 1 OF 1

SOLIDWORKS Educational Product. For Instructional Use Only.

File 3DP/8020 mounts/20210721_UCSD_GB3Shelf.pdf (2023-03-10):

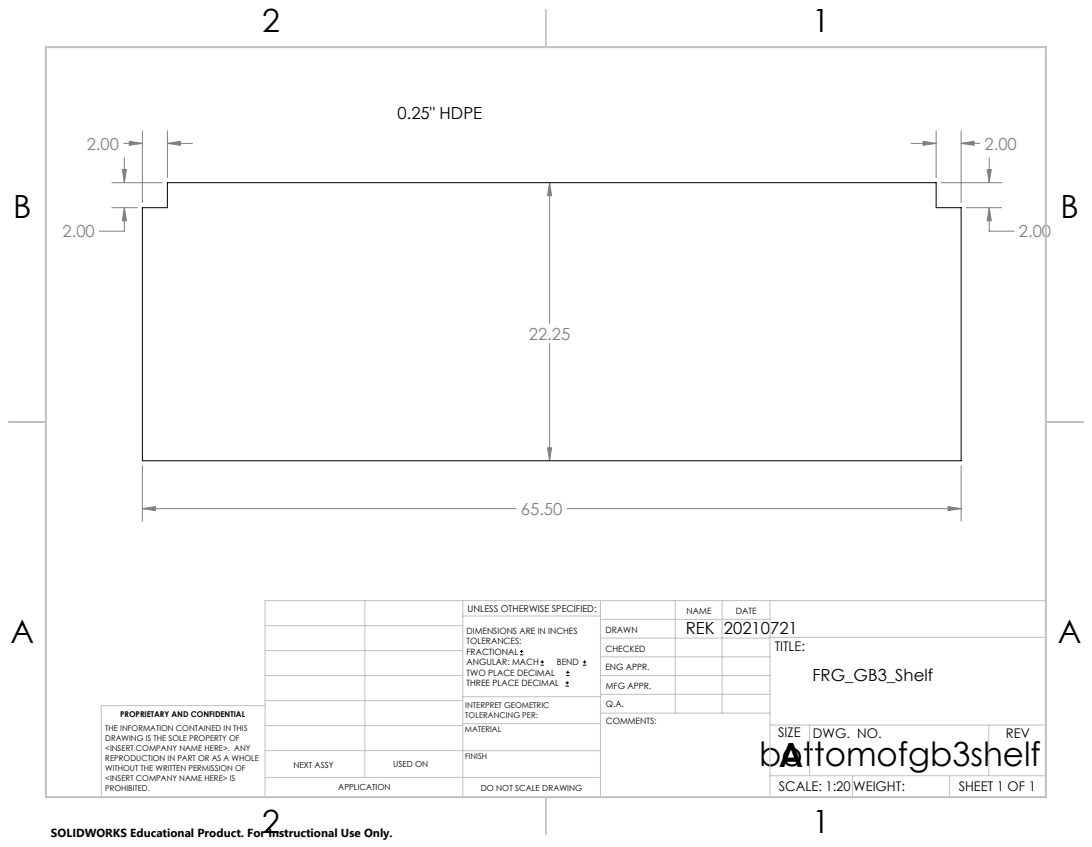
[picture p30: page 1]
0.25" HDPE

UNLESS OTHERWISE SPECIFIED: | | NAME | DATE
DIMENSIONS ARE IN INCHES TOLERANCES: FRACTIONAL ANGULAR: MACH BEND TWO PLACE DECIMAL THREE PLACE DECIMAL | DRAWN

CHECKED | | | TITLE: FRG_GB3_Shelf

ENG APPR.
MFG APPR.

INTERPRET GEOMETRIC TOLERANCING PER: | Q.A.
MATERIAL | bottomofgb3shelf | SIZE A | DWG. NO. | REV

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

NEXT ASSY | USED ON | FINISH

APPLICATION | DO NOT SCALE DRAWING | | SCALE: 1:20 WEIGHT: | | SHEET 1 OF 1

SOLIDWORKS Educational Product. For Instructional Use Only.

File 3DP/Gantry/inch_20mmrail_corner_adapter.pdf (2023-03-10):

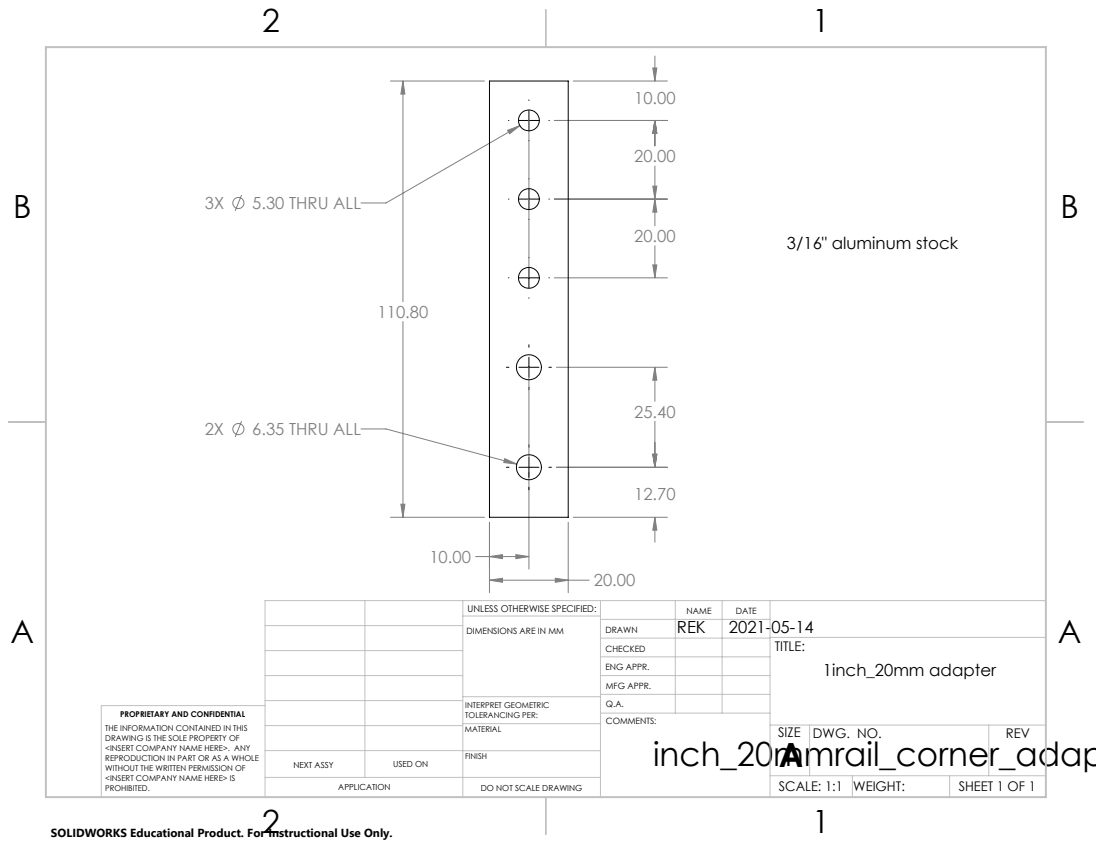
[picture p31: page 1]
5.30 THRU ALL; 6.35 THRU ALL; 3/16" aluminum stock

UNLESS OTHERWISE SPECIFIED: | | NAME | DATE
DIMENSIONS ARE IN MM | DRAWN | REK | 2021-05-14

CHECKED | | | TITLE: 1inch_20mm adapter

ENG APPR.
MFG APPR.

INTERPRET GEOMETRIC TOLERANCING PER: | Q.A.
MATERIAL | | SIZE A | DWG. NO. | REV

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

NEXT ASSY | USED ON | FINISH

APPLICATION | DO NOT SCALE DRAWING | | SCALE: 1:1 | WEIGHT: | SHEET 1 OF 1

SOLIDWORKS Educational Product. For Instructional Use Only.

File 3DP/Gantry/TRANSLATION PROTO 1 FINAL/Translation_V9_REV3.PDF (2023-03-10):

Project Abstract
This project sponsored by the Solar Energy Innovation Laboratory (SOLEIL) at UC San Diego focuses on the development of an automated system to increase the throughput and quality of the solar cells produced by the lab. SOLEIL is a group that researches materials for solar energy conversion and storage in an effort to further the advancement of renewable energy methods. The current manufacturing process for solar cells at SOLEIL requires extensive manual labor and provides a low throughput of twenty devices over the course of twelve hours. As such, the lab reached out to automate this process to reduce human intervention and increase the quality and amount of manufactured samples. Major requirements for the automated system include picking up solar cells and transferring them from station to station inside an enclosure. The final design solution for this project consists of a parallel gripper mounted onto a CNC-inspired translation system via a cantilever arm that deposits completed solar cell devices into storage trays. The gripper mechanism was able to meet its independent functional requirements by gripping and holding glass samples without inflicting damage. The translation system was able to provide resolutions of 0.2, 0.3, and 0.045 mm in x, y, and z directions, respectively.
A | A
B | B
C | C
D | D
MATERIAL | | SIZE D | DWG. NO. XXXXXXX | REV
NEXT ASSY | USED ON | FINISH
APPLICATION | DO NOT SCALE DRAWING | | SCALE: 1:10 WEIGHT: | | SHEET 1 OF 36
UNLESS OTHERWISE SPECIFIED: | | NAME | DATE
DIMENSIONS ARE IN MILLIMETERS TOLERANCES: FRACTIONAL ANGULAR: MACH BEND TWO PLACE DECIMAL THREE PLACE DECIMAL | DRAWN | Kieu Huynh06/05/20
| CHECKED | | | TITLE: TRANSLATION ROBOT
| ENG APPR.
| MFG APPR.
INTERPRET GEOMETRIC TOLERANCING PER: | Q.A.
COMMENTS:

PROPRIETARY AND CONFIDENTIAL THE INFORMATION CONTAINED IN THIS DRAWING IS THE SOLE PROPERTY OF <INSERT COMPANY NAME HERE>. ANY REPRODUCTION IN PART OR AS A WHOLE WITHOUT THE WRITTEN PERMISSION OF <INSERT COMPANY NAME HERE> IS PROHIBITED.
SOLIDWORKS Educational Product. For Instructional Use Only.

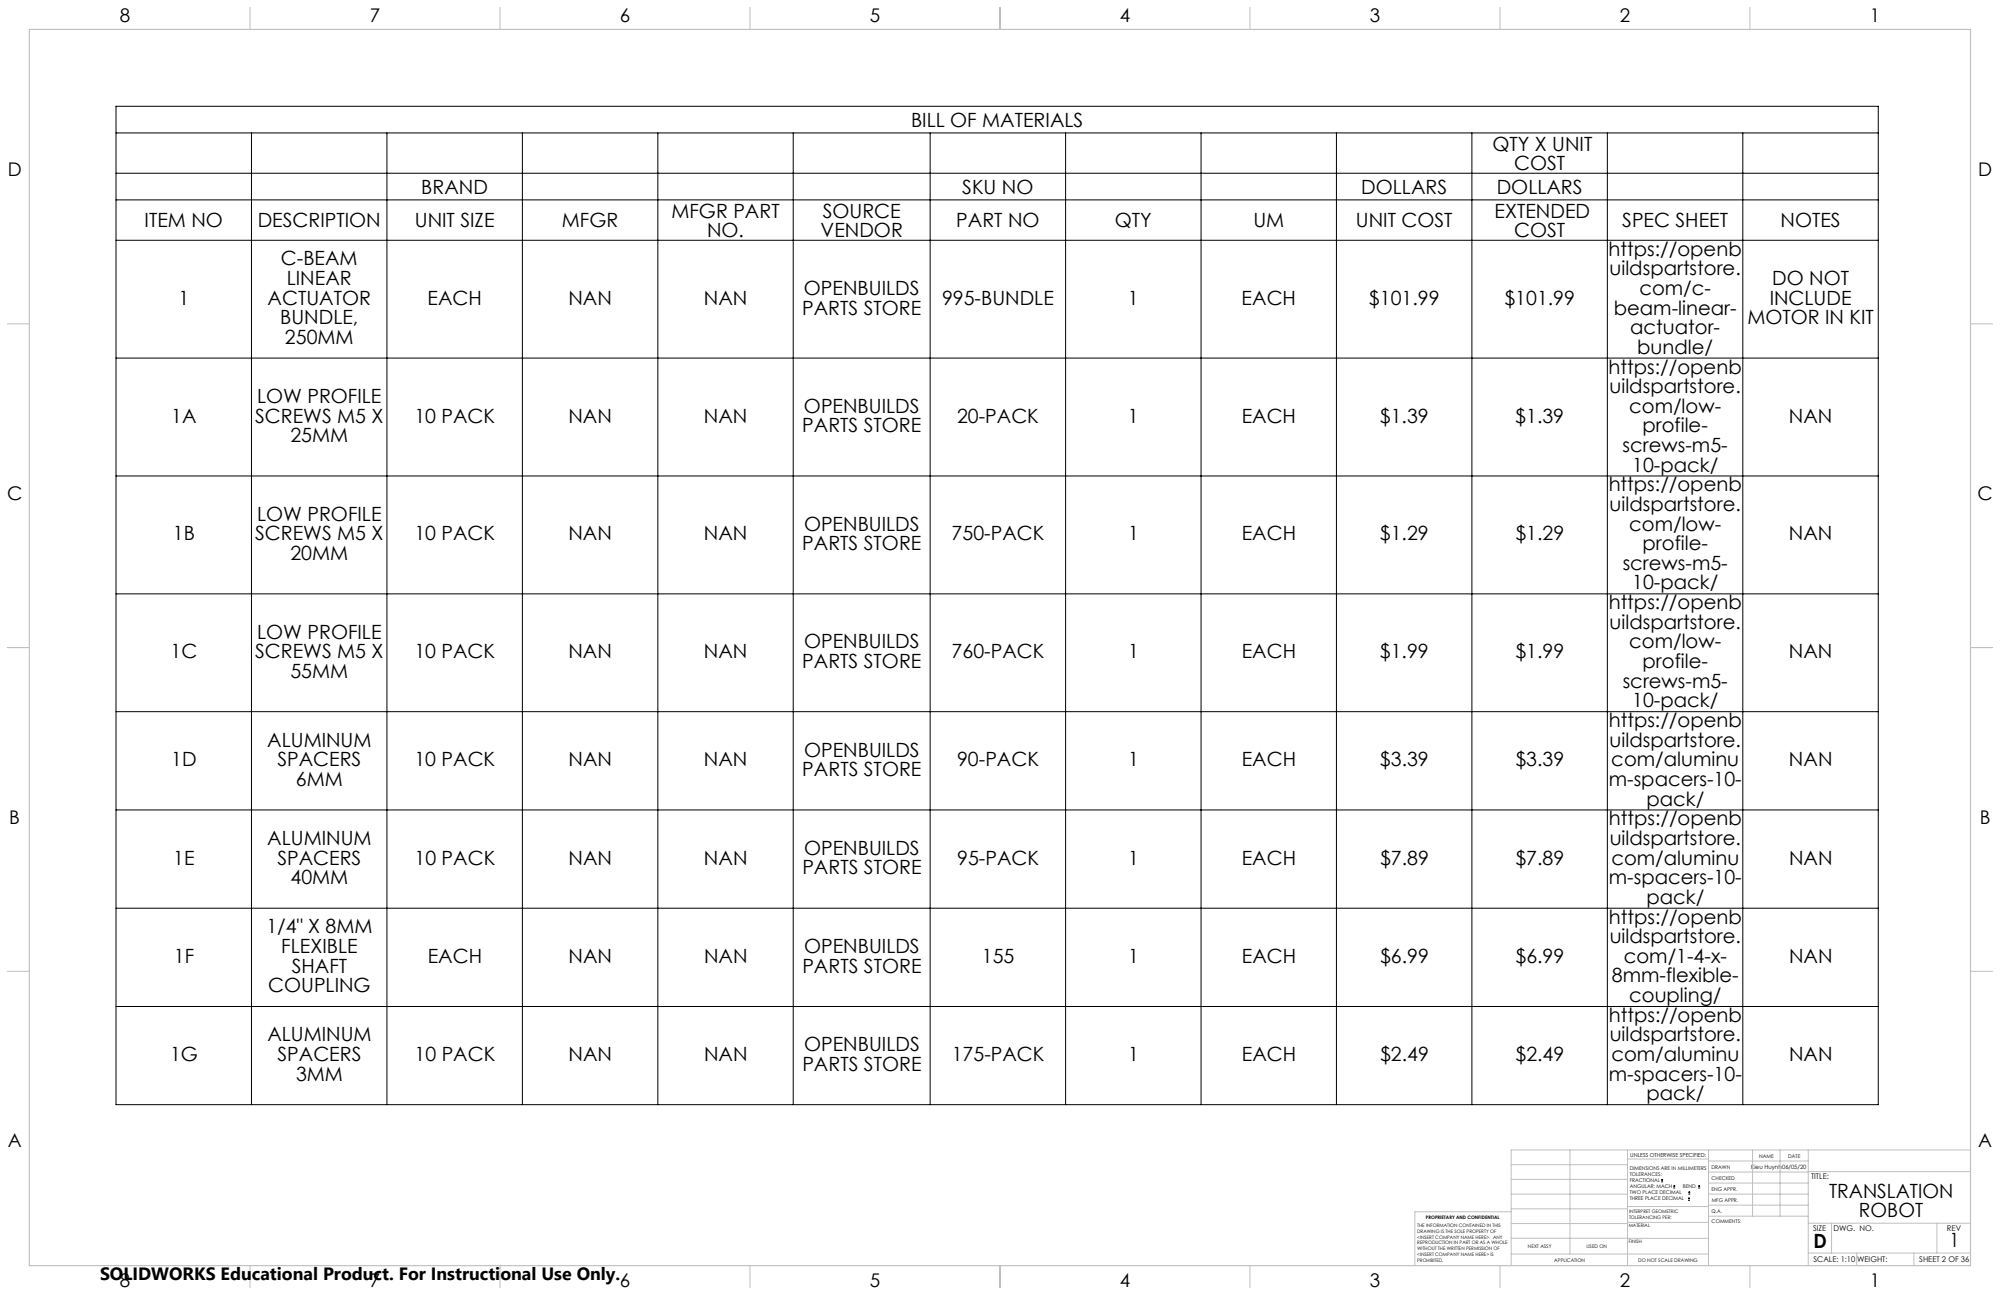
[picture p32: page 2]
DO NOT SCALE DRAWING; SHEET 2 OF 36

BILL OF MATERIALS

QTY X UNIT COST

BRAND | | | | SKU NO | | | DOLLARS | DOLLARS

ITEM NO | DESCRIPTION | UNIT SIZE | MFGR | MFGR PART NO. | VENDOR SOURCE | PART NO | QTY | UM | UNIT COST | EXTENDED COST | SPEC SHEET | NOTES
1 | C-BEAM LINEAR ACTUATOR BUNDLE, 250MM | EACH | NAN | NAN | OPENBUILDS PARTS STORE | 995-BUNDLE | 1 | EACH | $101.99 | $101.99 | https://openb uildspartstore. com/c-beam-linear-actuator-bundle/ | DO NOT INCLUDE MOTOR IN KIT

1A | LOW PROFILE SCREWS M5 X 25MM | 10 PACK | NAN | NAN | OPENBUILDS PARTS STORE | 20-PACK | 1 | EACH | $1.39 | $1.39 | https://openb uildspartstore. com/low-profile-screws-m5-10-pack/ | NAN

1B | LOW PROFILE SCREWS M5 X 20MM | 10 PACK | NAN | NAN | OPENBUILDS PARTS STORE | 750-PACK | 1 | EACH | $1.29 | $1.29 | https://openb uildspartstore. com/low-profile-screws-m5-10-pack/ | NAN

1C | LOW PROFILE SCREWS M5 X 55MM | 10 PACK | NAN | NAN | OPENBUILDS PARTS STORE | 760-PACK | 1 | EACH | $1.99 | $1.99 | https://openb uildspartstore. com/low-profile-screws-m5-10-pack/ | NAN

1D | ALUMINUM SPACERS 6MM | 10 PACK | NAN | NAN | OPENBUILDS PARTS STORE | 90-PACK | 1 | EACH | $3.39 | $3.39 | https://openb uildspartstore. com/aluminu m-spacers-10-pack/ | NAN

1E | ALUMINUM SPACERS 40MM | 10 PACK | NAN | NAN | OPENBUILDS PARTS STORE | 95-PACK | 1 | EACH | $7.89 | $7.89 | https://openb uildspartstore. com/aluminu m-spacers-10-pack/ | NAN

1F | 1/4" X 8MM FLEXIBLE SHAFT COUPLING | EACH | NAN | NAN | OPENBUILDS PARTS STORE | 155 | 1 | EACH | $6.99 | $6.99 | https://openb uildspartstore. com/1-4-x-8mm-flexible-coupling/ | NAN

1G | ALUMINUM SPACERS 3MM | 10 PACK | NAN | NAN | OPENBUILDS PARTS STORE | 175-PACK | 1 | EACH | $2.49 | $2.49 | https://openb uildspartstore. com/aluminu m-spacers-10-pack/ | NAN

UNLESS OTHERWISE SPECIFIED: | | NAME | DATE
DIMENSIONS ARE IN MILLIMETERS TOLERANCES: FRACTIONAL | DRAWN | Kieu Huynh06/05/20

CHECKED | | | TITLE: TRANSLATION

BILL OF MATERIALS

QTY X UNIT COST

BRAND | | | | SKU NO | | | DOLLARS | DOLLARS

ITEM NO | DESCRIPTION | UNIT SIZE | MFGR | MFGR PART NO. | VENDOR SOURCE | PART NO | QTY | UM | UNIT COST | EXTENDED COST | SPEC SHEET | NOTES
1H | SPACER 6MM ECCENTRIC | EACH | NAN | NAN | OPENBUILDS PARTS STORE | 226 | 2 | EACH | $1.99 | $3.98 | https://open buildspartstor e.com/ecce ntric-spacer/ | NAN
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

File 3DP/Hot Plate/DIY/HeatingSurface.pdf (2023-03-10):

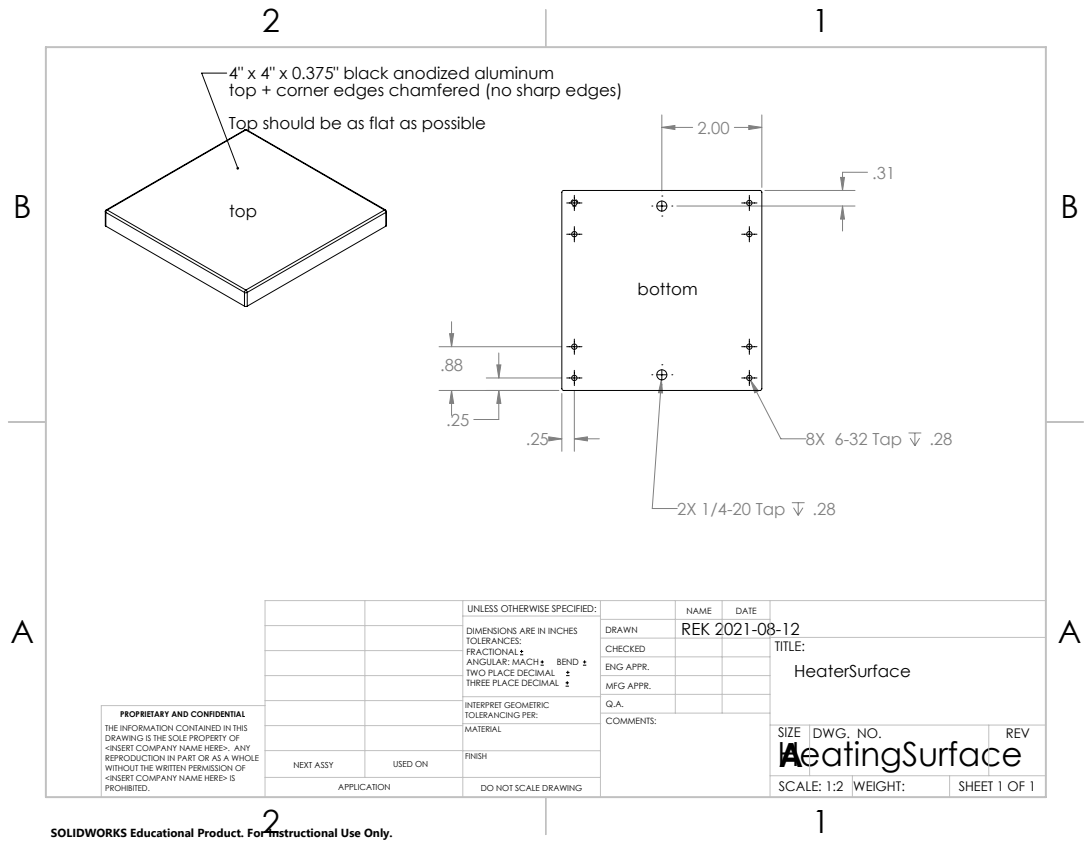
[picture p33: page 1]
8X 6-32 Tap .28; 2X 1/4-20 Tap .28

4" x 4" x 0.375" black anodized aluminum
top + corner edges chamfered (no sharp edges)
Top should be as flat as possible

UNLESS OTHERWISE SPECIFIED: | | NAME | DATE
DIMENSIONS ARE IN INCHES TOLERANCES: FRACTIONAL ANGULAR: MACH BEND TWO PLACE DECIMAL THREE PLACE DECIMAL | DRAWN | REK 2021-08-12

CHECKED | | | TITLE: HeaterSurface

ENG APPR.
MFG APPR.

INTERPRET GEOMETRIC TOLERANCING PER: | Q.A.
MATERIAL | | SIZE HeatingSurface A | DWG. NO. | REV

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

NEXT ASSY | USED ON | FINISH

APPLICATION | DO NOT SCALE DRAWING | | SCALE: 1:2 | WEIGHT: | SHEET 1 OF 1

SOLIDWORKS Educational Product. For Instructional Use Only.

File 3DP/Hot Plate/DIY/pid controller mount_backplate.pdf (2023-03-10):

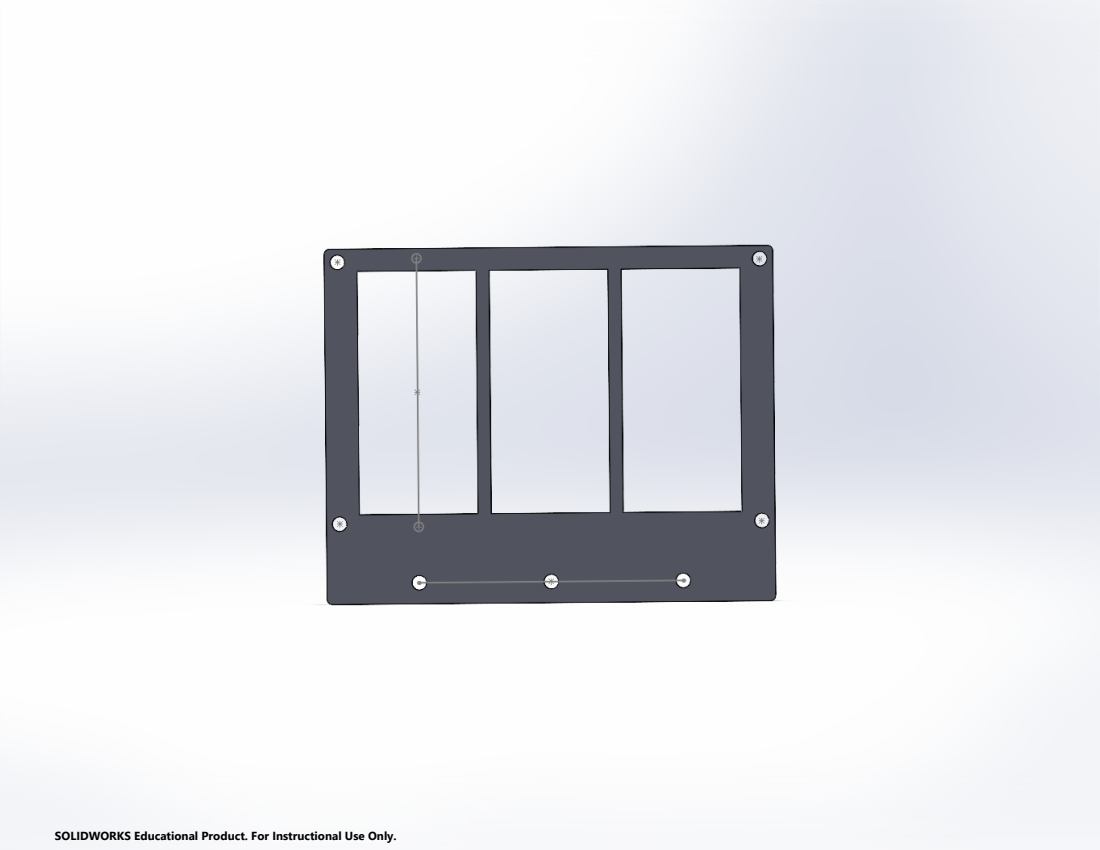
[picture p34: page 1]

SOLIDWORKS Educational Product. For Instructional Use Only.

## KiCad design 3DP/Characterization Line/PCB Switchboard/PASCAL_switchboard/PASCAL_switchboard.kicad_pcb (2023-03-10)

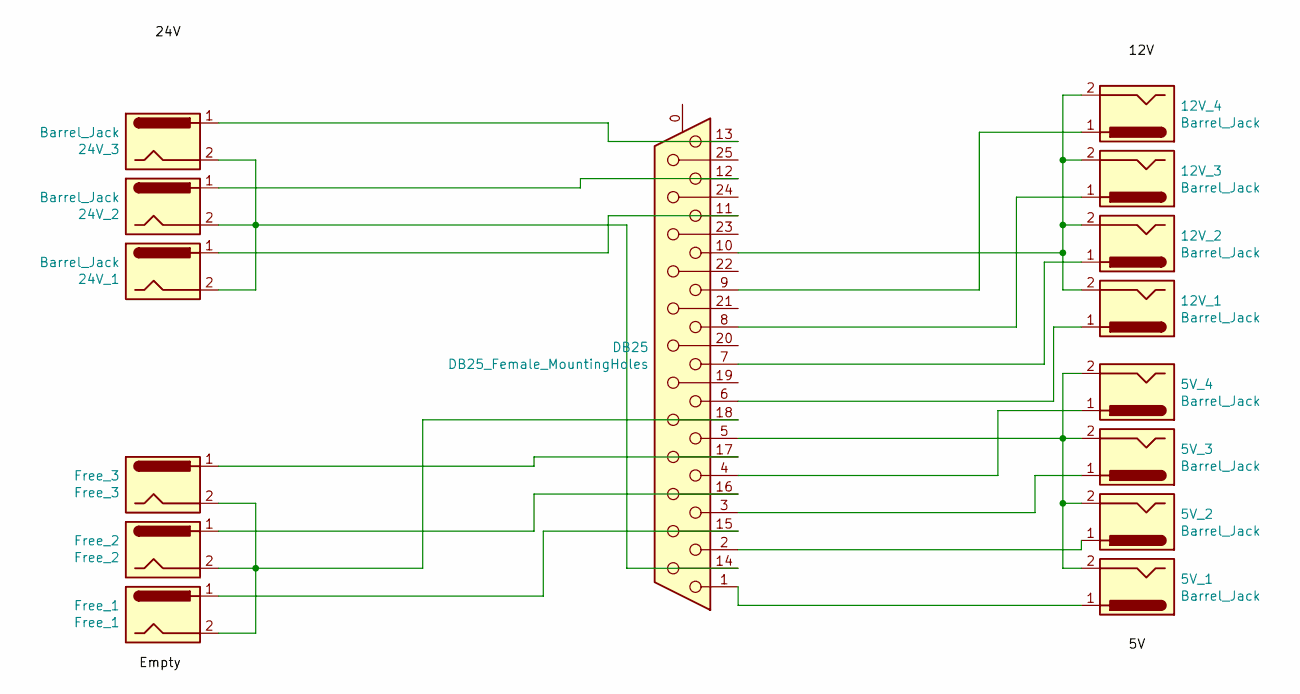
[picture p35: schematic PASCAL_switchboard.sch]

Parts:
5V_1, 5V_2, 5V_3, 5V_4, 12V_1, 12V_2, 12V_3, 12V_4, 24V_1, 24V_2, 24V_3: Barrel_Jack; BarrelJack_CUI_PJ-063AH_Horizontal
DB25: DB25_Female_MountingHoles; DSUB-25_Male_Horizontal_P2.77x2.84mm_EdgePinOffset7.70mm_Ho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
Free_1: Free_1; BarrelJack_CUI_PJ-063AH_Horizontal
Free_2: Free_2; BarrelJack_CUI_PJ-063AH_Horizontal
Free_3: Free_3; BarrelJack_CUI_PJ-063AH_Horizontal

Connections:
unnamed: 5V_1.1, DB25.1
unnamed: 5V_1.2, 5V_2.2, 5V_3.2, 5V_4.2, DB25.5
unnamed: 5V_2.1, DB25.2
unnamed: 5V_3.1, DB25.3
unnamed: 5V_4.1, DB25.4
unnamed: 12V_1.1, DB25.6
unnamed: 12V_1.2, 12V_2.2, 12V_3.2, 12V_4.2, DB25.10
unnamed: 12V_2.1, DB25.7
unnamed: 12V_3.1, DB25.8
unnamed: 12V_4.1, DB25.9
unnamed: 24V_1.1, DB25.11
unnamed: 24V_1.2, 24V_2.2, 24V_3.2, DB25.14
unnamed: 24V_2.1, DB25.12
unnamed: 24V_3.1, DB25.13
unnamed: DB25.15, Free_1.1
unnamed: DB25.16, Free_2.1
unnamed: DB25.17, Free_3.1
unnamed: DB25.18, Free_1.2, Free_2.2, Free_3.2

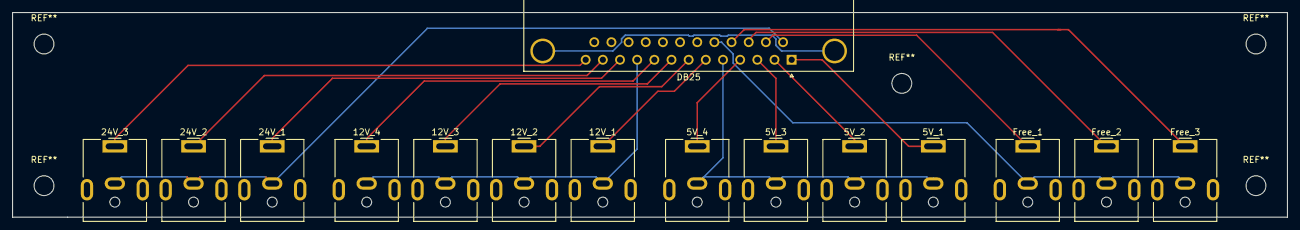
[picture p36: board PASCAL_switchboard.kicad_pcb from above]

Board: 2 copper layers, 205.7 x 33.0 mm, 15 parts (0 on the bottom side), 18 nets.

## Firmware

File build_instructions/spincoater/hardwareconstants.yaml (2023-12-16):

# Constants for the hardware modules that compose PASCAL
gantry:
  # communcation
  # serialid: "55838333932351108212" #LINUX ONLY hardware ID of gantry control board. Used to find correct COM port
  device_identifiers:
    vid: 7855 #vendor id, converted from hex to integer. WINDOWS ONLY can be determined by https://interworks.com/blog/ijahanshahi/2014/07/18/identify-vid-pid-usb-device/
    pid: 4 #product id, converted from hex to integer. WINDOWS ONLY. see link above
    location: "1-10" #WINDOWS
  pollingrate: 0.05 #delay (seconds) between sending a command and reading a response
  timeout: 15 #max time (seconds) allotted to gantry motion before flagging a movement error

  # movement
  positiontolerance: 0.05 #tolerance (mm) for movements to be considered complete
  speed_max: 10000 #max gantry speed, mm/min
  speed_min: 500 #min gantry speed, mm/min
  zhop_height: 10 #vertical clearance (mm) to use when moving between two points. will move this amount above the highest z point
  idle_coordinates: [192.25, 27.4, 82] #coordinates to move the gantry to when idle mid-process, mainly to avoid cameras
  clear_coordinates: [564.2, 254.3, 136.1] #coordinates to move the gantry out of the way for of glovebox operator
  opentrons_z: 83 #above this point, the gantry will collide with the opentrons frame
  opentrons_y: 195.3 #above this point, the gantry will collide with the opentrons frame
  opentrons_x: 190.5 #below this point, the gantry will enter the opentrons frame
  overall_gantry_limits:
    x_max: 567.0 #max x position (mm)
    x_min: 0 #min x position (mm)
    y_max: 282.0 #max y position (mm)
    y_min: 0 #min y position (mm)
    z_max: 166.0 #max z position (mm)
    z_min: 0 #min z position (mm)
  workspace_limits: #gantry limits in workspace frame
    x_max: 567.0 #max x position (mm)
    x_min: 192.25 #min x position (mm)
    y_max: 282.0 #max y position (mm)
    y_min: 0 #min y position (mm)
    z_max: 166.0 #max z position (mm)
    z_min: 0 #min z position (mm)
  opentrons_limits: #gantry limits in opentrons frame
    x_max: 192.25
    x_min: 0
    y_max: 200.7
    y_min: 8
    z_max: 82
    z_min: 0
  # transition_coordinates: [192.25, 195.3, 83] #coordinate to move to when transitioning between workspace and OT2 frames
  transition_coordinates: [192.25, 27.4, 82] #spincoater in deck slot 3

gripper:
  #communication
  device_identifiers:
    vid: 1027 #WINDOWS ONLY
    pid: 24597 #WINDOWS ONLY
    serial_number: "DN066QRWA"
  pollingrate: 0.05 #delay (seconds) between sending a command and reading a response
  timeout: 10 #max time (seconds) allotted to gripper motion before flagging a movement error
  width_max: 28.5 #maximum opening width (mm)
  width_min: 4.6 #minimum opening width (mm)
  pwm_max: 1300 #pulse width (us) corresponding to maximum width
  pwm_min: 740 #pulse width (us) corresponding to minimum width
  extra_opening_width_pick: 2.3 #extra width (mm) to open gripper when moving to pick up a sample
  extra_opening_width_place: 2.0 #extra width (mm) to open gripper when placing a sample. should be less than on picking!
  # slow_movement_interval: 0.7 #time (s) between intermediate servo setpoints when opening/closing slowly
  slow_interval: 7 #rate (us pwm/ 10 ms) to open at during "slow" setting
  fast_interval: 50 #rate to open at during "fast" setting
  idle_timeout: 30 #gripper idle time (seconds) after which automatically closes. To prevent servo burnout (fighting the spring to stay open)
  springs_loaded_threshold: 2000 #(650 original value) if the gripper load reading is below this value, we assume the springs are not applying load onto the gripper fingers (ie sample is clasped)
  catch_attempts: 3 #number of times to try picking up a sample before erroring out

hotplates:
  hp1:
    device_identifiers:
      vid: 1027
      pid: 24577
      serial_number: "AB0OYUYZA"
    address: 1 #rs485 address
    p0: [214.4, 73.3, 56.0]
  hp2:
    device_identifiers:
      vid: 1027
      pid: 24577
      serial_number: "AB0OYQKDA"
    address: 2
    p0: [214.2, 216.3, 55.0]
  hp3:
    device_identifiers:
      vid: 1027
      pid: 24577
      serial_number: "AB0OYQKPA"
    address: 3
    p0: [367.2, 217.3, 51.0]

liquidhandler:
  pollingrate: 0.1 #delay (seconds) between checks for new commands to push to liquid handler server
  timings:
    aspirate:
      preparetip: 10 #time (seconds) to pick up a fresh tip
      premix: # time (seconds) = (a*volume + b) * num_cycles
        a: 0.0209
        b: 0.5132
      slowretract: 3 #extra time to slowly retract pipette from well
      touchtip: 1.5 #time to touch tip/knock off droplets on side of well
      airgap: 2.5 #time to add an airgap
    travel: 2 #time to move from tiprack to aspiration well
    travel_slow: 4 #time to move if slow_travel active
    dispensedelay: 0.8 # time (seconds) between initiating a dispense command and the liquid beginning to hit the spincoating sample
    dispensedelay_slow: 1 #time to dispense *from staging position* if slow_travel active
  # dispense_delay: 1
  # aspiration_delay: 22.5  # time (seconds) to perform an aspiration and stage the pipette
  # staging_delay: 1.5  # time (seconds) to move pipette into position for drop staging
  server:
    ip: "169.254.160.20" #this is the external IP of the OT2 robot, can be found in the OT2 app!
    port: 8764

sampletray:
  p1: [494.0, 20.0, 67.3] #initial guess [x,y,z] coordinates for gantry to center over bottom left corner slot. Safer to overestimate z value here to avoid collisions
  p2: [404.7, 20.0, 67.3] #initial guess [x,y,z] coordinates for gantry to center over bottom left corner slot. Safer to overestimate z value here to avoid collisions
spincoater:
  # communication
  device_identifiers: #for the arduino controlling the vacuum solenoid
    # serialid: #LINUX ONLY "558383339323513140D1" #hardware ID of spincoater arduino. Used to find correct COM port
    vid: 2341 #WINDOWS ONLY
    pid: 0043 #WINDOWS ONLY
    serial_number: "95032303737351B01170"
  switchindex: "vacuumsolenoid" #key for switchbox relay that controls the vacuum solenoid (look at line ~32 in frgpascal.hardware.switchbox)
  communication_interval: 0.1 #delay (seconds) between communication to the odrive
  # movement
  p0: [4.6, 16.0, 62.1] #initial guess [x,y,z] coordinates for gantry to center over the chuck. Safer to overestimate z value here to avoid collisions
  rpm_max: 9000 #maximum angular velocity (rpm) the spincoater can hit
  rpm_min: 200 #minimum angular velocity (rpm) the spincoater can hit
  acceleration_max: 5000 #maximum angular acceleration (rpm/s) the spincoater can hit
  acceleration_min: 50 #maximum angular acceleration (rpm/s) the spincoater can hit
  logging_interval: 0.2 #interval (seconds) at which to log spincoating rpm
  vacuum_disengagement_time: 10 #delay (seconds) after closing vacuum solenoid -> vacuum releasing at the chuck
characterizationline:
  #movement
  axis:
    device_identifiers:
      vid: 7855 #WINDOWS ONLY
      pid: 4 #WINDOWS ONLY
      location: "1-1.3" #WINDOWS + GANTRY ONLY
    pollingrate: 0.05
    timeout: 20 #max time (seconds) to allow movement before flagging an error
    positiontolerance: 0.05 #tolerance (mm) for movements to be considered complete
    x_max: 400.0 #max x position (mm)
    x_min: 0 #min x position (mm)
    transfer_position: 0 #x coordinate to transfer samples to/from gantry
    p0: [563.5, 249.9, 63] #initial guess for coordinates for gantry to center over slot. safe to overestimate z here to avoid crashes
    traveltime: #polynomial y=mx+b to predict axis travel time (y, seconds) for a given distance (x, mm)
      m: 0.0461
      b: 1.161
  #hardware shared across stations
  switchbox:
    device_identifiers:
      vid: 10777
      pid: 3075
    pollingrate: 0.2
    relayresponsetime: 0.01 #seconds between telling relay to do something -> relay doing it
  shutter:
    device_identifiers:
      vid: 9025
      pid: 67
      serial_number: "95033313031351611262"
    pollingrate: 0.2
    max_change_time: 2 #max time to open/close transmission lamp shutter
  filterslider:
    device_identifiers:
      vid: 1027
      pid: 24597
      serial_number: "DK0AJS9DA"
    top: "2" #address/index for top shutter. This should be a string!
    bottom: "0" #address/index for bottom shutter. This should be a string!
    pollingrate: 0.2
    shutterresponsetime: 2 #seconds between telling the shutter to move -> shutter completing the move
  laser_settling_time: 0.5 #seconds for laser power to stabilize
  #individual stations
  stations:
    darkfield:
      cameraid: "12519"  #serial number for Thorlabs Camera
      position: 77.3 #position (mm) at which characterization axis centers sample in FOV
      switchindex: 9 #switchbox plug index for light source (ring light)
    pl_imaging:
      # cameraid: SAME AS DARKFIELD, NO NEED TO INPUT HERE #serial number for Thorlabs Camera #same camera as darkfield
      position: 77.3 #position (mm) at which characterization axis centers sample in FOV
      switchindex: 12 #switchbox plug index for light source (blue LED lamp)
    brightfield:
      cameraid: "12316" #serial number for Thorlabs Camera
      position: 161.6 #position (mm) at which characterization axis centers sample in FOV
      switchindex: 8 #switchbox plug index for light source (ring light)
    pl_blue: #spectroscopy
      position: 285.6
      switchindex: 5
      laser_settling_time: 0.2 #seconds for laser power to stabilize

    pl_red: #spectroscopy
      position: 285.6 #position (mm) at which characterization axis centers sample in FOV
      switchindex: 4 #switchbox plug index for light source (red laser)
      laser_settling_time: 0.2 #seconds for laser power to stabilize

    transmission: #spectroscopy
      position: 285.6 #position (mm) at which characterization axis centers sample in FOV
    #fourpointprobe:
    # position:397.5

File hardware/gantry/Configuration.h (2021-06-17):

/**
 * Marlin 3D Printer Firmware
 * Copyright (c) 2020 MarlinFirmware [https://github.com/MarlinFirmware/Marlin]
 *
 * Based on Sprinter and grbl.
 * Copyright (c) 2011 Camiel Gubbels / Erik van der Zalm
 *
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
 */
#pragma once

/**
 * Configuration.h
 *
 * Basic settings such as:
 *
 * - Type of electronics
 * - Type of temperature sensor
 * - Printer geometry
 * - Endstop configuration
 * - LCD controller
 * - Extra features
 *
 * Advanced settings can be found in Configuration_adv.h
 *
 */
#define CONFIGURATION_H_VERSION 020006

//===========================================================================
//============================= Getting Started =============================
//===========================================================================

/**
 * Here are some standard links for getting your machine calibrated:
 *
 * https://reprap.org/wiki/Calibration
 * https://youtu.be/wAL9d7FgInk
 * http://calculator.josefprusa.cz
 * https://reprap.org/wiki/Triffid_Hunter%27s_Calibration_Guide
 * https://www.thingiverse.com/thing:5573
 * https://sites.google.com/site/repraplogphase/calibration-of-your-reprap
 * https://www.thingiverse.com/thing:298812
 */

//===========================================================================
//============================= DELTA Printer ===============================
//===========================================================================
// For a Delta printer start with one of the configuration files in the
// config/examples/delta directory and customize for your machine.
//

//===========================================================================
//============================= SCARA Printer ===============================
//===========================================================================
// For a SCARA printer start with the configuration files in
// config/examples/SCARA and customize for your machine.
//

// @section info

// Author info of this build printed to the host during boot and M115
#define STRING_CONFIG_H_AUTHOR "(none, default config)" // Who made the changes.
//#define CUSTOM_VERSION_FILE Version.h // Path from the root directory (no quotes)

/**
 * *** VENDORS PLEASE READ ***
 *
 * Marlin allows you to add a custom boot image for Graphical LCDs.
 * With this option Marlin will first show your custom screen followed
 * by the standard Marlin logo with version number and web URL.
 *
 * We encourage you to take advantage of this new feature and we also
 * respectfully request that you retain the unmodified Marlin boot screen.
 */

// Show the Marlin bootscreen on startup. ** ENABLE FOR PRODUCTION **
// #define SHOW_BOOTSCREEN

// Show the bitmap in Marlin/_Bootscreen.h on startup.
//#define SHOW_CUSTOM_BOOTSCREEN

// Show the bitmap in Marlin/_Statusscreen.h on the status screen.
//#define CUSTOM_STATUS_SCREEN_IMAGE

// @section machine

/**
 * Select the serial port on the board to use for communication with the host.
 * This allows the connection of wireless adapters (for instance) to non-default port pins.
 * Serial port -1 is the USB emulated serial port, if available.
 * Note: The first serial port (-1 or 0) will always be used by the Arduino bootloader.
 *
 * :[-1, 0, 1, 2, 3, 4, 5, 6, 7]
 */
#define SERIAL_PORT -1

/**
 * Select a secondary serial port on the board to use for communication with the host.
 * :[-1, 0, 1, 2, 3, 4, 5, 6, 7]
 */
#define SERIAL_PORT_2 2

/**
 * This setting determines the communication speed of the printer.
 *
 * 250000 works in most cases, but you might try a lower speed if
 * you commonly experience drop-outs during host printing.
 * You may try up to 1000000 to speed up SD file transfer.
 *
 * :[2400, 9600, 19200, 38400, 57600, 115200, 250000, 500000, 1000000]
 */
#define BAUDRATE 115200

// Enable the Bluetooth serial interface on AT90USB devices
//#define BLUETOOTH

// Choose the name from boards.h that matches your setup
#ifndef MOTHERBOARD
  #define MOTHERBOARD BOARD_BTT_SKR_MINI_E3_V1_2
#endif

// Name displayed in the LCD "Ready" message and Info menu
#define CUSTOM_MACHINE_NAME "PASCAL-Gantry"

// Printer's unique ID, used by some programs to differentiate between machines.
// Choose your own or use a service like https://www.uuidgenerator.net/version4
//#define MACHINE_UUID "00000000-0000-0000-0000-000000000000"

// @section extruder

// This defines the number of extruders
// :[0, 1, 2, 3, 4, 5, 6, 7, 8]
#define EXTRUDERS 0

// Generally expected filament diameter (1.75, 2.85, 3.0, ...). Used for Volumetric, Filament Width Sensor, etc.
#define DEFAULT_NOMINAL_FILAMENT_DIA 1.75

// For Cyclops or any "multi-extruder" that shares a single nozzle.
//#define SINGLENOZZLE

// Save and restore temperature and fan speed on tool-change.
// Set standby for the unselected tool with M104/106/109 T...
#if ENABLED(SINGLENOZZLE)
  //#define SINGLENOZZLE_STANDBY_TEMP
  //#define SINGLENOZZLE_STANDBY_FAN
#endif
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

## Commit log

2020-06-30 Added firmware v5c
    version update consolidates functions of 2 seprate arduinos to enable both sensing and comunications in one board
2020-07-01 Now with PID control!
    Added PID control, with minimimal optimization on tuning parameters,
    RPM converges to setpoint within 10 seconds currenty. PID output manually fixed to output min of 1.8k rpm and max of 6.3k rpm.
2020-07-01 Update 6b with in line comments
    added additional comments to help break down reasoning for min value on PID controller, current only using PI control, D adds to much oscilations, need to look into method to enable ramping, and reco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
2020-07-01 added pid switch
    allows pid to start in off state, then turn on when a speed is givien, also enables z command to turn off device
2020-07-06 refactor gantry + communcation
    refactor gantry code to make motor control nonblocking to communication and processing of other commands. add gripper comms to python script
2020-09-01 compile firmware v1
    [MarlinMesh.scad]
2020-09-01 add servo
2020-09-01 increase stepper current
2020-09-03 moving average implementation, remove lcd + led code, header file
2020-09-03 big first update
    Initial push of maestro with some methods for defining workspace.
    - quaternion + centroid translation method for aligning workspaces (gantry - breadboard - labware)
    - working threaded webserver for triggering OT2, eventually reporting to dashboard
    - Labware object with inheritance from workspace, can be defined with position relative to breadboard position
    - spincoater routine rough draft
2020-10-13 add taskpacker example
    [dna_assembly.xls]
2020-10-14 sample tackpacker list
2021-02-17 new servo, quality of life
2021-02-17 full sample routine
2021-05-07 fix yaml loading on some modules, add gripper timeout daemon thread to gantry object
2021-05-27 update code to find serial devices on windows
2021-06-07 flir camera module
2021-06-08 start firmware for characterization axis
    [MarlinMesh.scad]
2021-06-08 build firmware for characterization axis
    [MarlinMesh.scad]
2021-06-17 reorganizing for install
    [dna_assembly.xls]
2021-06-22 calibration and hotplate update
2021-06-24 automate transition between frames
2021-07-08 truly working background threaded liquid handler
2021-07-08 worker threads
2021-07-08 working but uneccesary threading in lh
2021-07-19 calibrations and such
2021-07-23 experiment planning with most functions separate
    [stock_solutions.csv]
2021-08-05 update calibrations + positions
2021-08-06 testing the scheduler
    [stock_solutions.csv]
2021-08-06 example experiment to test
    [stock_solutions.csv]
2021-08-07 first working version!!!
    [stock_solutions.csv]
2021-08-09 some fixes
    [stock_solutions.csv]
2021-08-10 working + proper calibrations
2021-08-12 insert idle_gantry steps if idling over hotplate
    [stock_solutions.csv]
2021-08-18 tuning constants
    [stock_solutions.csv]
2021-08-23 move camera exposure time to variable
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2021-09-02 plot solution map during planning
    [stock_solutions.csv]
2021-09-02 working example notebook
    [stock_solutions.csv]
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2021-09-03 working much better
    [stock_solutions.csv]
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2021-09-15 adjust worker code to accomodate task format changes
    [stock_solutions.csv]
2021-09-15 sample experiment
    [stock_solutions.csv]
2021-09-16 updated schedule
    [stock_solutions.csv]
2021-09-16 unique task id upon task deepcopy
    [stock_solutions.csv]
2021-09-17 clean up the planning notebook
    [stock_solutions.csv]
2021-09-17 improved example worklist development
    [stock_solutions.csv]
2021-09-20 working generalized
    [stock_solutions.csv]
2021-09-23 planning stuff
    [stock_solutions.csv]
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2021-10-05 autopopulate protocol file with labware defined in planning notebook
    [stock_solutions.csv]
2021-10-05 reusable tips
    [stock_solutions.csv]
2021-10-05 set starting tips on tipracks!
    [stock_solutions.csv]
2021-10-05 finalize protocol with tip reuse
    [Example Experiment_stocksolutions.csv, stock_solutions.csv]
2021-10-05 finalize the solution planning notebook
    [Example Experiment_stocksolutions.csv]
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2022-02-03 subclass workers, tasks, notebook still works
    [SampleDataframe_Deniz Absorbers for Passivation.csv, stocksolutions_Deniz Absorbers for Passivation.csv, weight_table.csv]
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2022-02-03 schedulign working in notebook
    [SampleDataframe_Deniz Absorbers for Passivation.csv, stocksolutions_Deniz Absorbers for Passivation.csv, weight_table.csv]
2022-02-03 working test notebook
    [SampleDataframe_Deniz Absorbers for Passivation.csv]
2022-02-03 working in notebook
    [SampleDataframe_Deniz Absorbers for Passivation.csv, dna_assembly.xls]
2022-02-03 working again
    [SampleDataframe_Deniz Absorbers for Passivation.csv, stocksolutions_Deniz Absorbers for Passivation.csv, weight_table.csv]
2022-02-03 characterization stations accept kwargs
    [SampleDataframe_Deniz Absorbers for Passivation.csv, stocksolutions_Deniz Absorbers for Passivation.csv, weight_table.csv]
2022-02-03 characterization baseline instruction file
    [SampleDataframe_Deniz Absorbers for Passivation.csv, stocksolutions_Deniz Absorbers for Passivation.csv, weight_table.csv]
2022-02-03 Squashed commit of the following:
    commit fa8cdf94e3cad32ec0d78d3d54f6a67ef78eb468
    Author: rishi-e-kumar <47284667+rishi-e-kumar@users.noreply.github.com>
    Date: Wed Feb 2 15:40:29 2022 -0800
    working
    commit e35d37d27c6338b7ca871381f260f28f3cfbacd0
    Author: rishi-e-kumar <47284667+rishi-e-kumar@users.noreply.github.com>
    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
    [SampleDataframe_Deniz Absorbers for Passivation.csv, stocksolutions_Deniz Absorbers for Passivation.csv, weight_table.csv]
2022-02-16 add hotplates to netlist
    [SampleDataframe_Deniz Absorbers for Passivation.csv, stocksolutions_Deniz Absorbers for Passivation.csv, weight_table.csv]
2022-02-16 assign correct hotplate, tray workers to anneal,rest tasks
    [SampleDataframe_Deniz Absorbers for Passivation.csv, stocksolutions_Deniz Absorbers for Passivation.csv, weight_table.csv]
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2022-03-04 update the example experiment
    [sampledataframe_experiment name.csv, stocksolutions_experiment name.csv]
2022-03-16 fix brightfield homo, remove sample checker in Client
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2022-03-31 change breakpoint logic
    [sampledataframe_experiment name.csv, stocksolutions_experiment name.csv]
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2022-05-12 fix Sample worklist deepcopy
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2022-10-06 swapping the cameras for bf and df/plimage
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2023-03-10 added 3d printed parts for safe keeping
    [.75mm Washer.sldprt, 1 inch magnet slot.SLDPRT, 1 inch magnet slot.STL, 1.sldprt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]
2023-07-12 Update OT2Listener_1000left300right.py
    addressing leaking pipette during pre_mixing
2024-04-07 cad files
    [base_machined.SLDPRT, base_machined.STL]
2024-05-13 change filename
    [base_machined.SLDPRT, base_machined.STL]
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2025-06-11 workspace frame transition fixes
    attempt 1 of repairing gantry transition across OT2/non-OT2 target_frames.
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2025-08-22 opentrons stop shaking
    decreases the speed of opentrons pipette arm x-y motions, plus some fixes for the humanoperator functionality.
2025-09-04 Gantry stop crashing, PASCALPlanner cross-compatibility fix
    PASCALPlanner failed to work on MacOS due to requiring the wmi package within frgpascal/hardware/helpers.py Not necessary if only going to write the input files without actually running PASCAL. Gantr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
2025-11-16 Spincoater, Opentrons, Gantry updates
    Added functionality for using the lights on opentrons during a run, for updating/replacing the gantry control board firmware, and for including/bypassing the Worker_SpincoaterLiquidHandler() in case 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
2025-11-18 spincoater dummy error fix
    slight typo in the "skip spincoater" logic that caused a meaningless error statement to print in the command prompt during bootup.
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2026-02-24 fixed Gantry()._waitformovement() logic
    changes line 525 to control when to start communicating with the output position response of the gantry as it moves, depending on whether the gantry's control is through serial or socket connections.
2026-02-28 first pass at abstracting Gantry to work immediately when swapping control boards
    The legacy gantry relied on a BigTreeTech SKR Mini E3 V2.0 control board, my efforts to update the x-axis to be more stable/reproducible requires upgrading to external closed-loop control drivers con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
2026-03-17 calibrations, ip issues.
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2026-03-27 tray calibration issues
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2026-03-30 updated logic for sample place onto a sampletray
    Now GantryGripper will move to the destination slot on a sample tray, attempt to release the sample, then move slightly upwards ~0.1-0.15mm and open gripper 5% more to loose the gripper in case it st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
2026-04-24 changed duet board connections to eliminate crash failure mode
    Was possible for a user to close the PASCAL prompt but leave the Duet board powered on, and then restart the PASCAL prompt, without actually flushing any in-progress motion commands from the Duet boa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
2026-05-30 calibrations, bug squashing
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

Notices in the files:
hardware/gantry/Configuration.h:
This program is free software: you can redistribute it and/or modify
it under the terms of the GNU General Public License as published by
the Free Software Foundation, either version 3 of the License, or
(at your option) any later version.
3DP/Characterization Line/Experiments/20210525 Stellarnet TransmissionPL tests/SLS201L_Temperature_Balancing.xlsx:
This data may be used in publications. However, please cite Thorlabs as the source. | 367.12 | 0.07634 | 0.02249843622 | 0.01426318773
